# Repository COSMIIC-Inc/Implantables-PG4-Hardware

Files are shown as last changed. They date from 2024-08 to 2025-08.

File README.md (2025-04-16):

# Implantables-PG4-Hardware Read Me

## Contents
This repository is home to the 3D CAD and PCB design files of the PG4 - Pulse Generator Module in the COSMIIC System.
Further documentation is available at **[docs.cosmiic.org/Implantables/PG4-Module](https://docs.cosmiic.org/Implantables/PG4-Module)**

## Licensing
Hardware-related files are licensed to open source users by COSMIIC under the CERN Open Hardware License - Permissive - v2 (CERN-OHL-P-2.0). Refer to the **[license text](https://ohwr.org/cern_ohl_p_v2.txt)** (also embedded in the repository as **LICENSE.txt**) and **[user guide](https://ohwr.org/project/cernohl/-/wikis/uploads/8a6b5d01f71c207c49493e4d114d61e6/cern_ohl_p_v2_howto.pdf)** to understand your permissions.

Hardware-related files includes, but is not limited to...

- Mechanical Design
    - 3D CAD Files (parts and assemblies, multiple file types)
    - Mechanical Drawings (parts and assemblies, mulitple file types)
- PCB Design
    - Fabrication (Gerber and Drill files)
    - Assembly (Pick and Place, BOM)
    - Archive (Schematics, multiple file types)

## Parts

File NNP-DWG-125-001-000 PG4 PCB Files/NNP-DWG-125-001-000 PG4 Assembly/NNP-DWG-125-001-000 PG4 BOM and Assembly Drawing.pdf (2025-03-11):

D | D

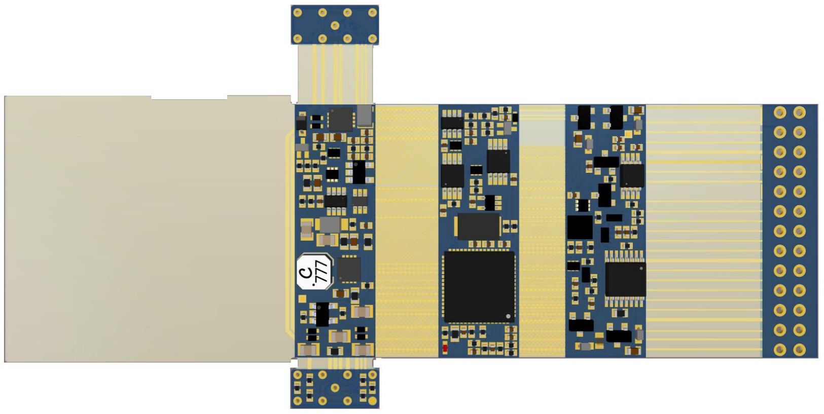
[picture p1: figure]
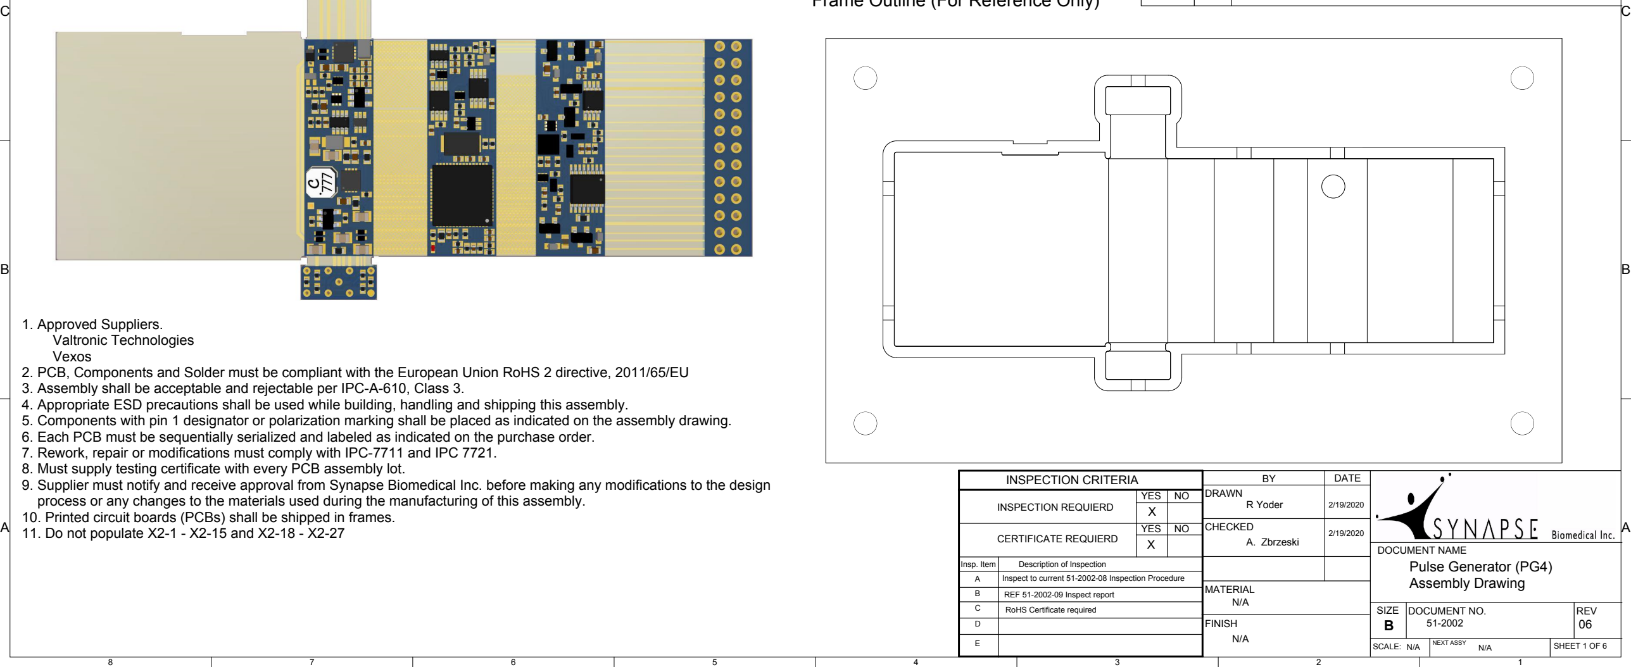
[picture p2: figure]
1. Approved Suppliers. Valtronic Technologies Vexos; CHECKED A. Zbrzeski; DRAWN R Yoder; Pulse Generator (PG4) Assembly Drawing; DOCUMENT NAME; DOCUMENT NO.; REV; NEXT ASSY; SCALE:; SIZE; FINISH; MATERIAL; DATE; SHEET 1 OF 6; RoHS Certificate required; Insp. Item; Description of Inspection; CERTIFICATE REQUIERD; YES; INSPECTION REQUIERD; INSPECTION CRITERIA; REF 51-2002-09 Inspect report

2. PCB, Components and Solder must be compliant with the European Union RoHS 2 directive, 2011/65/EU
3. Assembly shall be acceptable and rejectable per IPC-A-610, Class 3.
4. Appropriate ESD precautions shall be used while building, handling and shipping this assembly.
5. Components with pin 1 designator or polarization marking shall be placed as indicated on the assembly drawing.
6. Each PCB must be sequentially serialized and labeled as indicated on the purchase order.
7. Rework, repair or modifications must comply with IPC-7711 and IPC 7721.
8. Must supply testing certificate with every PCB assembly lot.
9. Supplier must notify and receive approval from Synapse Biomedical Inc. before making any modifications to the design
process or any changes to the materials used during the manufacturing of this assembly.
10. Printed circuit boards (PCBs) shall be shipped in frames.
11. Do not populate X2-1 - X2-15 and X2-18 - X2-27 | 2/19/2020
ECN | REV | DESCRIPTION

DCN-105
01 | Initial Engineering Release, Never Built
| 02 | Updated manufacture notes.Never released
| 03
- Updated BOM (refer to Page 1 of the Schematic for changes)
- Added component placement.
- Added Frame and PCB outline drawing.
- Added instructions for serial number sticker.

DCN-108

DCN-109 04
- Update BOM (Revision 5 of 52-2002)
- Added Quantity (Qty) column to BOM
- Corrected Note 8 Manufacture note defining test certificate

## Top Side View (For Reference Only)

- Updated notes
- Added text to Page 1 indicating that the drawings were top side view and for reference only.
- Changed text in the Material, Finish, Scale and Next Assy blocks to N/A
- Added Pin 1 designators to the components on the component placement drawing (Page 5)
- Changed component U24 from a SC70-3 package to a
SOT23-3 package to match footprint on the PCB
- Inspection Criteria box added to drawing.
- Requirements added to the Inspection Criteria Box.

DCN-119 05

## Frame Outline (For Reference Only)

A | Inspect to current 51-2002-08 Inspection Procedure

06

- Changed C33 from a 330pF to 330nF (0.33uF)
- Item 15 on BOM (02-19-2020)

D | D
C | C
B | B
A | A
DRAWN R Yoder | 2/19/2020
CHECKED A. Zbrzeski | 2/19/2020

Pulse Generator (PG4)

DOCUMENT NAME

BY | DATE

Item

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
Designator
Ref.

Ref.

Ref.

C1, C6
C2, C14, C15, C30, C38,
C40, C41, C42
C3, C5, C29
C4
C7, C8, C9, C10, C13, C18, C20, C22, C23, C24, C25,
C26, C28, C32, C34, C43,
C44, C45, C47
C11
C12, C17, C46, C48, C49
C16
C19, C21
C27
C31
C33
D1, D2, D3, D4, D5, D6, D7 D8

D9, D10, D11, D12
L1
L2
L3
LED1

Q1, Q2

Q3, Q4, Q5, Q6, Q7

R1, R2, R4, R5, R7, R8, R10, R11, R13

SBI
51-2002-01_03

52-2002_05

51-2002-07_01

56-0036
53-0037

53-0038
53-0039
53-0040

53-0041-1
53-0042
53-0043
53-0044
53-0041-2
53-0041-3
53-0047
54-0075
54-0076

54-0077
53-0032
53-0033
53-0034
53-0035

54-0050

54-0051

53-0048

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
Description
51-2002-01_03 Pulse Generator (PG4) Schematic Drawing
52-2002_05, NNP Pulse Generator PCB, Unpopulated
51-2002-07_01 Pulse Generator (PG4) Pick and Place File
0.1uF, 100V, X7R, 0805, 10%, RoHS 1uF, 50V, X5R, 10%, 0603, RoHS

47uF, 10V, X5R, 20%, 0805, RoHS 10uF, 6.3V, X5R, 0603_20%, RoHS 0.1uF, 16V, X7R, 0402, RoHS

68pF, 50V, C0G, 0402, 5%, RoHS 4.7uF, 6.3V, X5R, 20%, 0402, RoHS 0.001uF, 50V, X7R, 20%, 0402, RoHS 8pF, 50V, C0G, 0402, 10%, RoHS 1000pF, 50V, C0G, 5%, 0402, RoHS 10pF, 50V, C0G, 5%, 0402, RoHS 0.33uF, 50V, X7R, 10%, 0805, RoHS Schotty Diode, 30V, 100mA, RoHS Schottky Diode, 100V, 150mA, SOD323, RoHS
Zener Diode, 4.7V, 150 mW, 0603, RoHS 100uH, 270mA, 20%, RoHS
470uH, 35mA, 10%, RoHS
33uH, 120mA, 10%, RoHS
LED, Red, 0402, 20mA ,2V, 140mcd, RoHS
PNP, -50V, -100mA, SOT523, 150MHz, RoHS
N-Channel MOSFET, 50V, 300mA, SOT23, RoHS
0.0 ohm, 1/16W, 0402, RoHS

Manufacturer

N/A

N/A

Murata Electronics North America Murata Electronics North America

Murata Electronics North America Murata Electronics North America AVX Corporation

Murata Electronics North America Murata Electronics North America Murata Electronics North America Murata Electronics North America Murata Electronics North America Murata Electronics North America Murata Electronics North America Panasonic Electronic Components STMicroelectronics

Comchip Technology
TDK Corporation
Taiyo Yuden
TDK Corporation
Lumex Opto/Components Inc.

Panasonic Electronic Components

Diodes Incorporated

Vishay Dale

Manufacturer Part Number

N/A

N/A

GCM21BR72A104KA37K
GRT188R61H105KE13D

GRM21BR61A476ME15L
GRM188R60J106ME47J
04023C104KAT2A

GRM1555C1H680JA01D
GRM155R60J475ME47D
GJM1555C1H1R0BB01D
GRM1555C1H8R0DA01D
GRM1555C1H102JA01D
GRM1555C1H100JA01D
GRM219R71H334KA88D
DB2731600L
BAT46JFILM

CZRU52C4V7
VLCF5020T-101MR27
CB2518T471K
NLCV25T-330K-PF
SML-LX0402SIC-TR

DSA9001S0L

DMN5L06K-7

CRCW04020000Z0ED

Suggested Supplier

Innovative Circuits

N/A

Digi-Key
Digi-Key

Digi-Key
Digi-Key
Digi-Key

Digi-Key
Digi-Key
Digi-Key
Digi-Key
Digi-Key
Digi-Key
Digi-Key
Digi-Key
Digi-Key

Digi-Key
Digi-Key
Digi-Key
Digi-Key
Digi-Key

Digi-Key

Digi-Key

Digi-Key

Supplier Part Number

N/A

N/A

490-8051-6-ND
490-12330-6-ND

490-9961-6-ND
490-6405-6-ND
478-7868-6-ND

490-5876-6-ND
490-5915-6-ND
490-6073-6-ND
490-5867-6-ND
490-3244-6-ND
490-5921-6-ND
490-3327-6-ND
DB2731600LDKR-ND
497-6653-6-ND

641-1028-6-ND
445-3203-6-ND
587-2194-6-ND
445-1759-6-ND
67-1878-6-ND

DSA9001S0LDKR-ND

DMN5L06KDIDKR-ND

541-0.0JDKR-ND

D | D
C | C
B | B
A | A
BY | DATE
DRAWN R Yoder | 2/19/2020
CHECKED A. Zbrzeski | 2/19/2020

DOCUMENT NAME
Pulse Generator (PG4)

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
R15, R16, R34, R47, R48,
R60
R17, R22, R23, R24, R27,
R30, R46
R18

R19, R25, R26, R28
R20, R21

R29
R31, R38, R40, R41, R42,
R57, R58, R59, R61, R62,
R63, R64, R65, R66
R32, R35, R36, R39, R43

R37, R52

R44

R45, R56

R49
R51
R53
R54
R67
RV1
U1
U2, U3

U4

U5

53-0049-1
53-0050

53-0049-2

53-0049-3

53-0049-4
53-0049-5

53-0051
53-0049-7

53-0049-8

53-0049-9

53-0049-10

53-0049-11

53-0049-12
53-0049-13
53-0049-14
53-0049-15
53-0049-16
53-0066
54-0052
54-0053

54-0054

54-0055

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
0.1 ohm, 1%, 1/16W, 0402, RoHS 0.0 ohm, 1/10W, 0603, RoHS

49.9k ohm, 1%, 1/16W, 0402, RoHS

470k ohm, 1% , 1/16W, smd, 0402, RoHS
1.0k ohm, 1%, 1/16W, smd, 0402, RoHS 5.1K ohm, 1%, 1/16W, smd, 0402, RoHS
84.5k ohm, 1%, 1/10W, 0402, RoHS 100k ohm, 1%, 1/16W, smd, 0402, RoHS

10.0k ohm, 1%, 1/16W, smd, 0402, RoHS
15.0k ohm, 1%, 1/16W, smd, 0402, RoHS
1.6K ohm, 1%, 1/16W, smd, 0402, RoHS
150k ohm, 1%, 1/16W, smd, 0402, RoHS
10 ohm, 1%, 1/16W, 0402, RoHS 20k ohm, 1%, 1/16W, 0402, RoHS 953k ohm, 1%, 1/16W, 0402, RoHS 36k ohm , 1%, 1/16W, 0402, RoHS 56 ohm, 0.1%, 1/16W, 0402, RoHS MOV, 12V, 0603, RoHS
Current Monitor, 2.5V-20V, 1%, RoHS Step Down DC-DC, 4.5V-45V, 50mA, RoHS
Comparator, 2.7-5.5V, 40nS, SOT23-8, RoHS
XOR, 1.65-5.5V, uPAK6, RoHS

Vishay Dale
Vishay Dale

Vishay Dale

Vishay Dale

Vishay Dale
Vishay Dale

Vishay Dale
Vishay Dale

Vishay Dale

Vishay Dale

Vishay Dale

Vishay Dale

Vishay Dale
Vishay Dale
Vishay Dale
Vishay Dale
Vishay Dale
BOURNS
Diodes Incorporated
Linear Technology

Maxim Integrated

Fairchild Semiconductor

RCWE0402R100FNEA
CRCW06030000Z0EA

CRCW040249K9FKED

CRCW0402470KFKED

CRCW04021K00FKED
CRCW04025K10FKED

CRCW040284K5FKED
CRCW0402100KFKED

CRCW040210K0FKED

CRCW040215K0FKED

CRCW04021K60FKED

CRCW0402150KFKED

CRCW040210R0FKED
CRCW040220K0FKED
CRCW0402953RFKED
CRCW040236K0FKED
CRCW040256R0FKED
CG0603MLC-12E
ZXCT1010E5TA
LTC3642EDD-3.3#PBF

MAX9142EKA+T

NC7SZ86L6X

Digi-Key
Digi-Key

Digi-Key

Digi-Key

Digi-Key
Digi-Key

Digi-Key
Digi-Key

Digi-Key

Digi-Key

Digi-Key

Digi-Key

Digi-Key
Digi-Key
Digi-Key
Digi-Key
Digi-Key
Digi-Key
Digi-Key
Digi-Key

Digi-Key

Digi-Key

541-2711-6-ND
541-0.0GDKR-ND

541-49.9KLDKR-ND

541-470KLDKR-ND

541-1.00KLDKR-ND
541-5.10KLDKR-ND

541-84.5KLDKR-ND
541-100KLDKR-ND

541-10.0KLDKR-ND

541-15.0KLDKR-ND

541-1.60KLDKR-ND

541-150KLDKR-ND

541-10.0LDKR-ND
541-20.0KLDKR-ND
541-953LDKR-ND
541-36.0KLDKR-ND
541-56.0LDKR-ND
CG0603MLC-12EDKR-ND
ZXCT1010DKR-ND
LTC3642EDD-3.3#PBF-ND

MAX9142EKA+TDKR-ND

NC7SZ86L6XDKR-ND

D | D
C | C
B | B
A | A
DRAWN R Yoder | 2/19/2020
CHECKED A. Zbrzeski | 2/19/2020

Pulse Generator (PG4)

DOCUMENT NAME

BY | DATE

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
U20, U21

U22
U23
U24
Y1

54-0056
54-0057
54-0058
54-0059

54-0060
54-0061

54-0062

54-0074

54-0063

54-0064

54-0065
54-0066
54-0067

54-0068

54-0069

54-0070
54-0071
54-0072
54-0073

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
Digital Isolator, 3-5.5V, uSOP8, RoHS Silicon delay, 3-3.6V, uSOP8, RoHS FLIPFLOP, 1.65-5.5V, uPAk6, RoHS Low Droupout negative regulator, -5V, -200mA, RoHS
Voltage detector Reset, SC70-5, RoHS uC, 2.7-5.5V, 8bit, QFN64, RoHS

Temperature Sensor,12bit I2C, SOT563, RoHS
Tri-axis accelerometer, I2C, LGA10, RoHS
BOOST, 2.3-10V, TSOT23-8, RoHS

DAC 2V5 internal reference, RoHS

2-Input NOR, 1.65-5.5V, uPak6, RoHS MOSFET 2N, 60V, 0.305A, RoHS 2-Input Positive OR, 1.65-5.5V, uBGA8, RoHS
Analog Switch, 10ohm, QUAD SPST, TSSOP16, RoHS
Dual 2-Input NOR, 1.65-5.5V, uBGA8, RoHS
UHS Buffer Tri-State, uPAK6, RoHS DAC 10bit, uSOP8, RoHS
REF 1.25V, 3.9uA, SOT23-3, RoHS Crystal 8MHz SMT, RoHS

NVE Corp/Isolation Products Maxim Integrated
Fairchild Semiconductor
Linear Technology

Texas Instruments
Atmel

Texas Instruments

Kionix

Linear Technology

Linear Technology

Fairchild Semiconductor
Vishay Siliconix
Texas Instruments

Maxim Integrated

Texas Instruments

Fairchild Semiconductor
Maxim Integrated
Texas Instruments
NDK

IL712-1E
DS1100LU-500+
NC7SZ175L6X
LT1964IS5-BYP#TRMPBF

TPS3805H33DCKR
AT90CAN128-16MU

TMP112AIDRLT

KXTE9-2050

LT3464ETS8#TRMPBF

LTC2630CSC6-LM12#TRMPBF

NC7SZ02L6X
SI1026X-T1-GE3
SN74LVC2G32YZPR

MAX313LCUE+

SN74LVC2G02YZPR

NC7SZ126L6X
MAX5355CUA+
REF3312AIDBZR
NX5032GA-8.000M-STD-CSU-1

Digi-Key
Digi-Key
Digi-Key
Digi-Key

Digi-Key
Digi-Key

Digi-Key

Mouser

Digi-Key

Digi-Key

Digi-Key
Digi-Key
Digi-Key

Digi-Key

Digi-Key

Digi-Key
Digi-Key
Digi-Key
Digi-Key

390-1105-5-ND
DS1100LU-500+-ND
NC7SZ175L6XFSDKR-ND
LT1964IS5-
BYP#TRMPBFCT-ND
296-13407-6-ND
AT90CAN128-16MURDKR-ND
296-24621-6-ND

912-KXTE9-2050

LT3464ETS8#TRMPBFDKR-ND
LTC2630CSC6-
LM12#TRMPBFDKR-ND
NC7SZ02L6XDKR-ND
SI1026X-T1-GE3CT-ND
296-15350-1-ND

MAX313LCUE+-ND

296-18799-6-ND

NC7SZ126L6XFSDKR-ND
MAX5355CUA+-ND
296-41484-6-ND
644-1132-6-ND

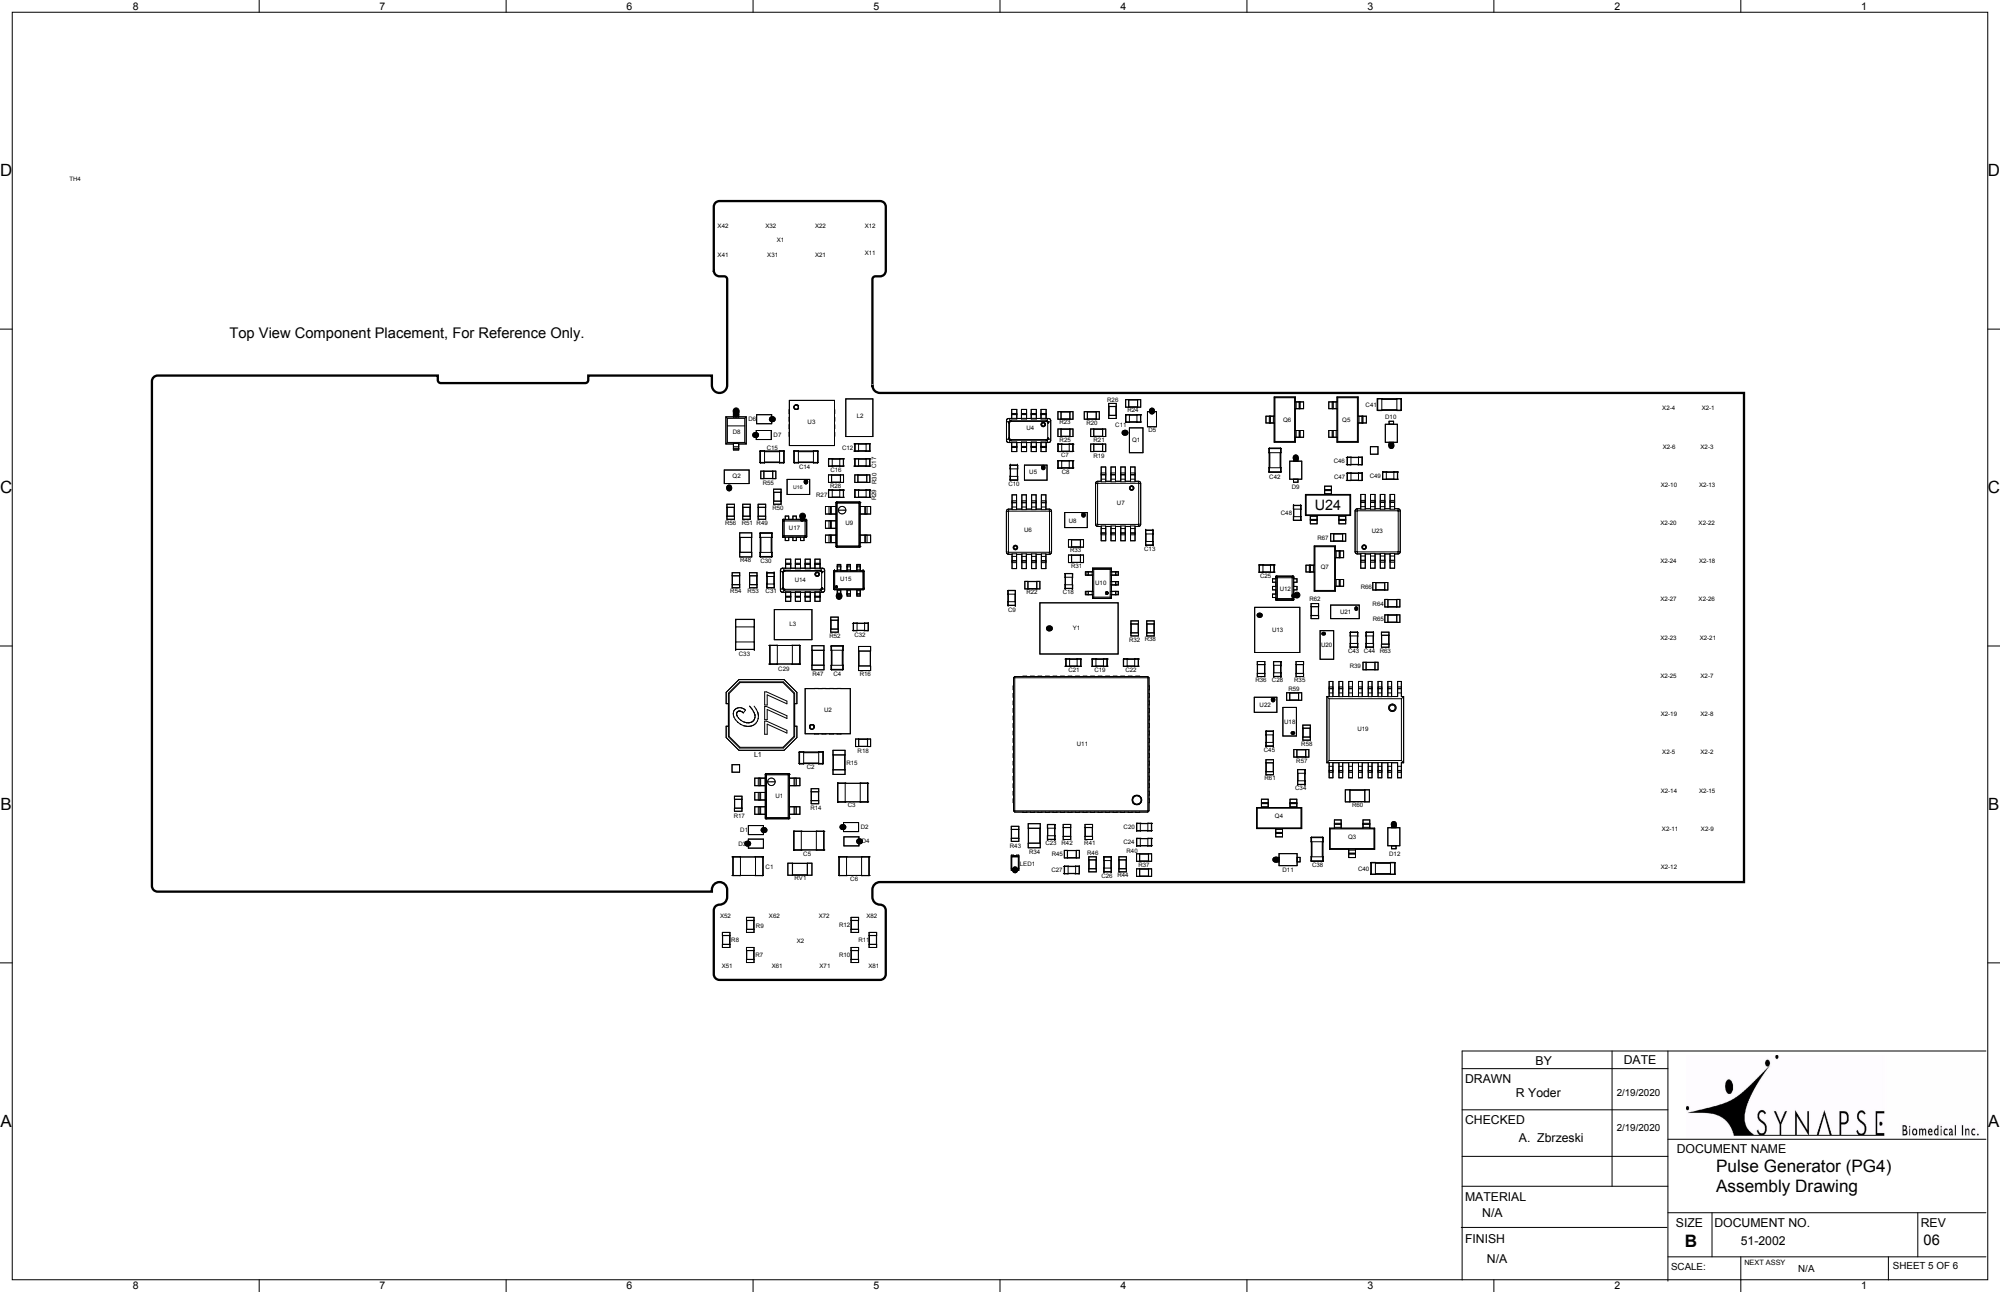
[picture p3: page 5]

Top View Component Placement, For Reference Only.

DRAWN R Yoder | 2/19/2020

CHECKED A. Zbrzeski | 2/19/2020

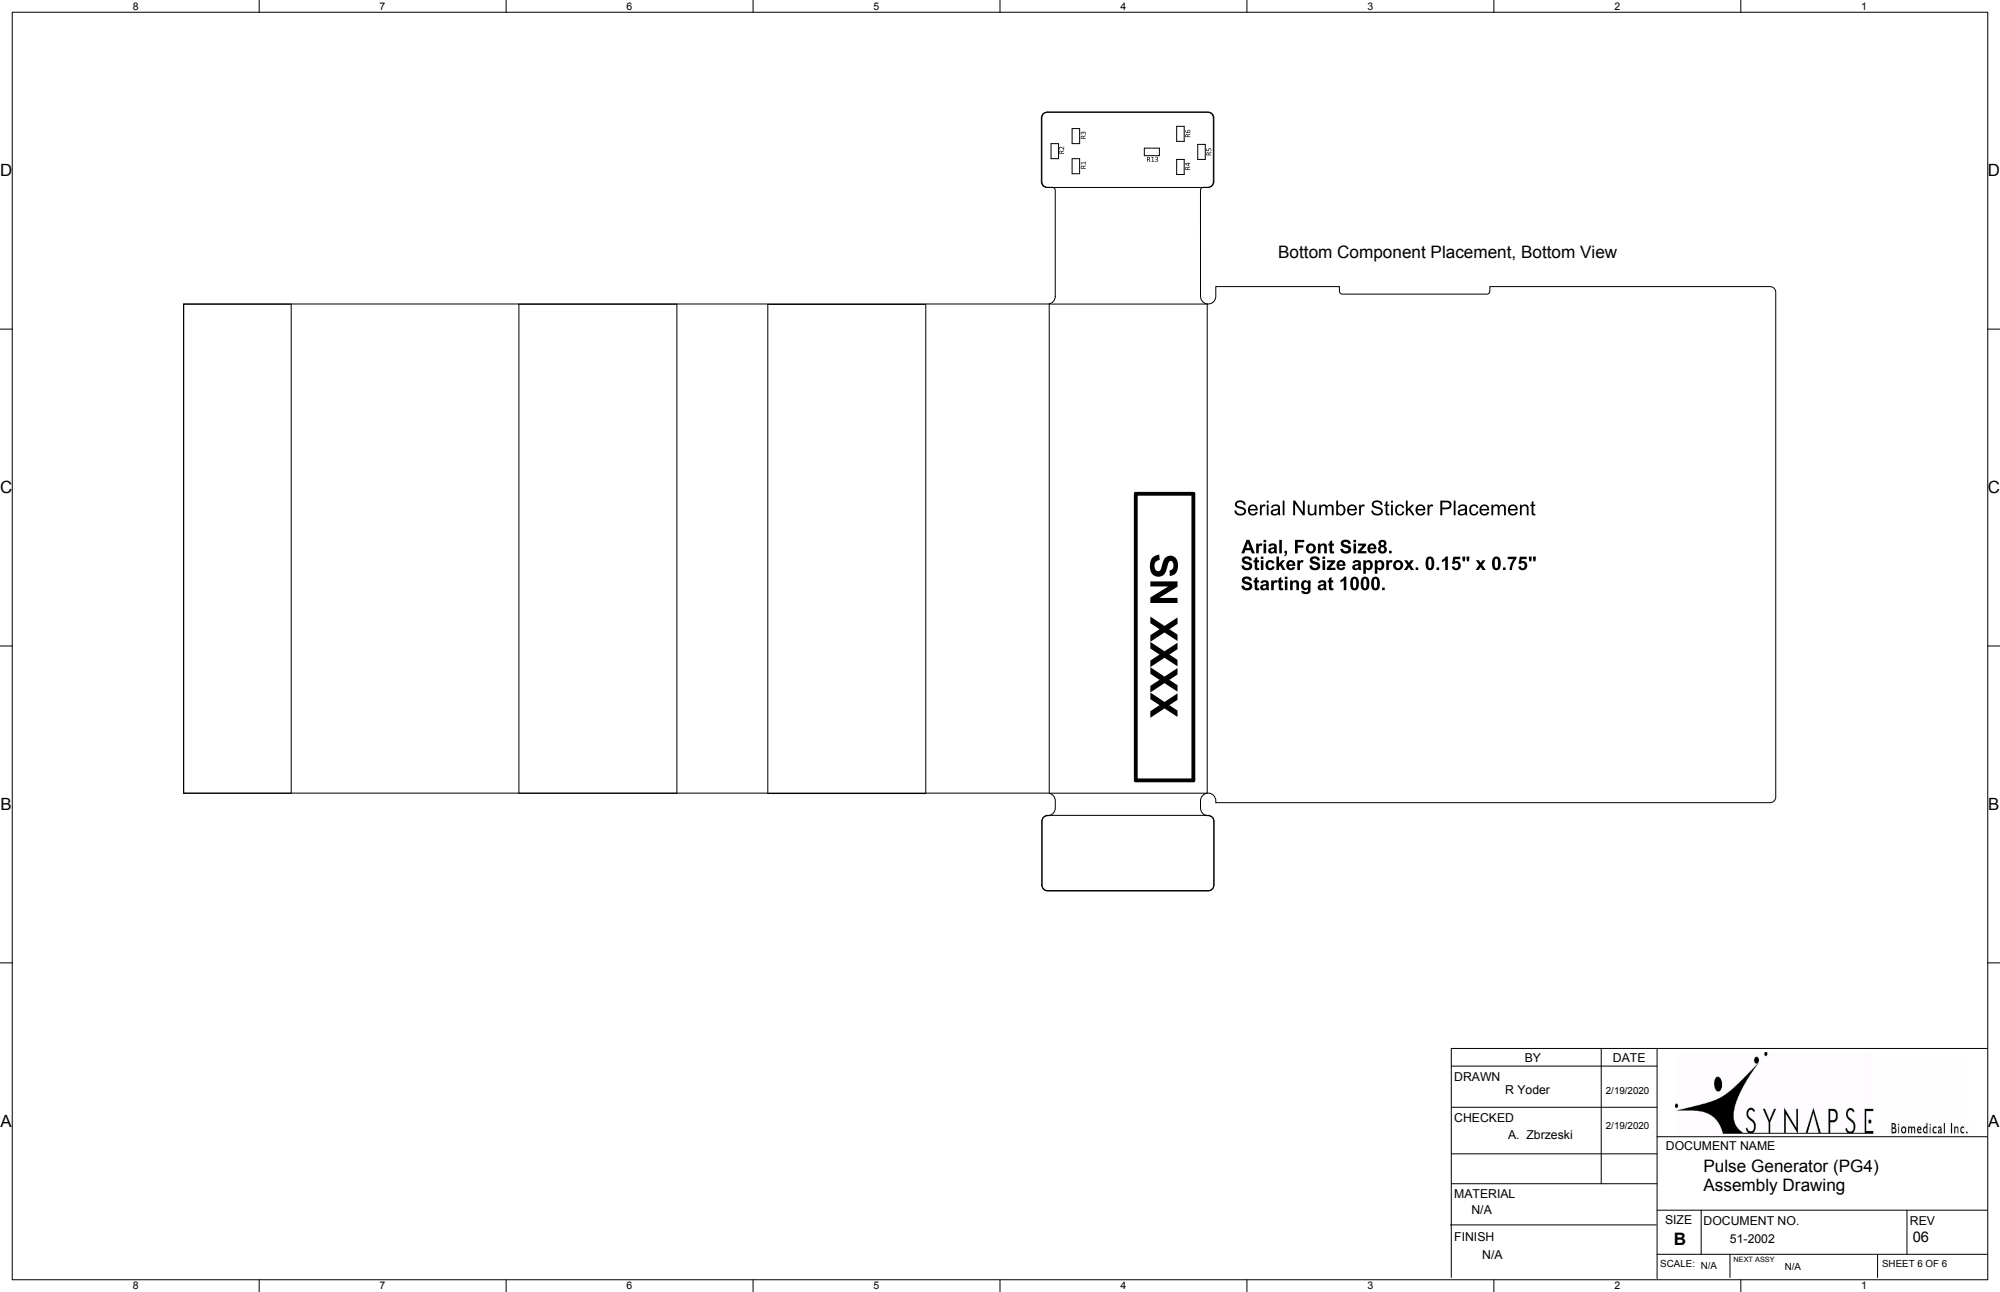
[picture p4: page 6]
DATE; DOCUMENT NAME Pulse Generator (PG4)

Bottom Component Placement, Bottom View

DRAWN R Yoder | 2/19/2020

CHECKED A. Zbrzeski | 2/19/2020

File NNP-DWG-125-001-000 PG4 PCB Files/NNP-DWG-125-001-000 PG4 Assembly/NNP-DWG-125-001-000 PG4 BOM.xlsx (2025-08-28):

Designator | Description | Quantity | MFR | MPN | Supplier 1 | Supplier Part Number 1 | Footprint
C1, C6 | 0.1uF, 100V, X7R, 0805, 10%, RoHS | 2 | AVX | 08051C104KAZ2A | Digi-Key | 478-3562-1-ND (https://octopart-clicks.com/click/altium?manufacturer=AVX%20Corporation&mpn=08051C104KAZ2A&seller=Digi-Key&sku=478-3562-1-ND&country=US&channel=BOM%20Report) | CAP_0805
C12, C19, C48, C50, C51 | 4.7uF, 6.3V, X5R, 20%, 0402, RoHS | 5 | Panasonic | ECJ-0EB0J475M | Digi-Key | PCC2475CT-ND (https://octopart-clicks.com/click/altium?manufacturer=Panasonic%20Electronic%20Components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) | CAP_0402
C13 | 68pF, 50V, C0G, 0402, 5%, RoHS | 1 | Murata | GRM1555C1H680JZ01D | Digi-Key | 490-1289-1-ND (https://octopart-clicks.com/click/altium?mpn=GRM1555C1H680JZ01D&seller=Digi-Key&sku=490-1289-1-ND&country=US&channel=BOM%20Report) | CAP_0402
C17 | 0.001uF, 50V, X7R, 20%, 0402, RoHS | 1 | Kemet | C0402C103M5RACTU | Digi-Key | 399-7760-2-ND (https://octopart-clicks.com/click/altium?manufacturer=Kemet&mpn=C0402C103M5RACTU&seller=Digi-Key&sku=399-7760-2-ND&country=US&channel=BOM%20Report) | CAP_0402
C2, C14, C15, C33, C37, C38, C39, C40, C41, C42, C43, C44 | 1uF, 50V, X5R, 10%, 0603, RoHS | 12 | Taiyo Yuden | UMK107BJ105KA-T | Digi-Key | 587-2400-1-ND (https://octopart-clicks.com/click/altium?manufacturer=Taiyo%20Yuden&mpn=UMK107BJ105KA-T&seller=Digi-Key&sku=587-2400-1-ND&country=US&channel=BOM%20Report) | CAP_0603
C21, C23 | 8pF, 50V, C0G, 0402, 10%, RoHS | 2 | Panasonic | ECJ-0EC1H080D | Digi-Key | PCC080CQCT-ND (https://octopart-clicks.com/click/altium?manufacturer=Panasonic%20Electronic%20Components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) | CAP_0402
C29 | 1000pF, 50V, C0G, 5%, 0402, RoHS | 1 | Murata | GRM1555C1H102JA01D | Digi-Key | 490-3244-1-ND (https://octopart-clicks.com/click/altium?mpn=GRM1555C1H102JA01D&seller=Digi-Key&sku=490-3244-1-ND&country=US&channel=BOM%20Report) | CAP_0402
C32 | 10pF, 50V, C0G, 5%, 0402, RoHS | 1 | Murata | GRM1555C1H100JZ01 | Digi-Key | 490-1278-1-ND (https://octopart-clicks.com/click/altium?mpn=GRM1555C1H100JZ01D&seller=Digi-Key&sku=490-1278-1-ND&country=US&channel=BOM%20Report) | CAP_0402
C35 | 0.33uF, 50V, X7R, 10%, 0805, RoHS | 1 | Murata | GRM219R71H334KA88D | Digi-Key | 490-3327-1-ND (https://octopart-clicks.com/click/altium?mpn=GRM219R71H334KA88D&seller=Digi-Key&sku=490-3327-1-ND&country=US&channel=BOM%20Report) | CAP_0805
C4 | 10uF, 6.3V, X5R, 0603_20%, RoHS | 1 | Panasonic | ECJ-1VB0J106M | Digi-Key | PCC2395CT-ND (https://octopart-clicks.com/click/altium?manufacturer=Panasonic%20Electronic%20Components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) | CAP_0603
C3, C5, C31 | 47uF 10V, X5R, 20%, 0805, RoHS | 3 | TDK | C2012X5R1A476M125AC | Digi-Key | 445-8239-6-ND (https://octopart-clicks.com/click/altium?manufacturer=TDK%20Corporation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) | CAP_0805
C7, C8, C9, C10, C11, C20, C22, C24, C25, C26, C27, C28, C30, C34, C36, C45, C46, C47, C49 | 0.1uF, 16V, X7R, 0402, RoHS | 19 | Murata | GRM155R71C104KA88D | Digi-Key | 490-3261-2-ND (https://octopart-clicks.com/click/altium?mpn=GRM155R71C104KA88D&seller=Digi-Key&sku=490-3261-2-ND&country=US&channel=BOM%20Report) | CAP_0402
D1, D2, D3, D4, D5, D6, D7 | Schotty Diode, 30V, 100mA, RoHS | 7 | Panasonic | DB27316 | Digi-Key | DB2731600LCT-ND (https://octopart-clicks.com/click/altium?manufacturer=Panasonic%20Electronic%20Components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) | SSSMini2-F4-B
D8 | Schottky Diode, 100V, 150mA, SOD323, RoHS | 1 | STMicroelectronics | BAT46JFILM | Digi-Key | 497-6653-1-ND (https://octopart-clicks.com/click/altium?manufacturer=STMicroelectronics&mpn=BAT46JFILM&seller=Digi-Key&sku=497-6653-1-ND&country=US&channel=BOM%20Report) | SOD323
L1 | 100uH, 270mA, 20%, RoHS | 1 | TDK | LPS4414-104MLC | Digi-Key | 445-3203-1-ND (https://octopart-clicks.com/click/altium?manufacturer=TDK%20Corporation&mpn=VLCF5020T-101MR27&seller=Digi-Key&sku=445-3203-1-ND&country=US&channel=BOM%20Report) | IND-LPS4414
L2 | 470uH, 35mA, 10%, RoHS | 1 | Taiyo Yuden | CB2518T471K | Digi-Key | 587-2194-6-ND (https://octopart-clicks.com/click/altium?manufacturer=Taiyo%20Yuden&mpn=CB2518T471K&seller=Digi-Key&sku=587-2194-6-ND&country=US&channel=BOM%20Report) | IND_1007
L3 | 33uH, 120mA, 10%, RoHS | 1 | Panasonic | ELJ-PC330KF | Digi-Key | PCD1096CT-ND (https://octopart-clicks.com/click/altium?manufacturer=Panasonic%20Electronic%20Components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) | IND_1008
LED1 | LED, Red, 0402, 20mA ,2V, 140mcd, RoHS | 1 | Lumex | SML-LX0402SIC-TR | Digi-Key | 67-1878-1-ND (https://octopart-clicks.com/click/altium?manufacturer=Lumex%20Opto%2FComponents%20Inc.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) | LED_0402_RED
Q1, Q2 | PNP, -50V, -100mA, SOT523, 150MHz, RoHS | 2 | Panasonic | DSA9001S0L | Digi-Key | DSA9001S0LDKR-ND (https://octopart-clicks.com/click/altium?manufacturer=Panasonic%20Electronic%20Components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) | SOT523
Q3, Q4, Q5, Q6, Q7 | N-Channel MOSFET, 50V, 300mA, SOT23, RoHS | 5 | Diodes Inc. | DMN5L06K-7 | Digi-Key | DMN5L06KDICT-ND (https://octopart-clicks.com/click/altium?manufacturer=Diodes%20Incorporated&mpn=DMN5L06K-7&seller=Digi-Key&sku=DMN5L06KDICT-ND&country=US&channel=BOM%20Report) | SOT23-3
R? | 84.5k ohm, 1%, 1/10W, 0402, RoHS | 1 | Panasonic | ERJ-2RKF8452X | Digi-Key | P84.5KLTR-ND (https://octopart-clicks.com/click/altium?manufacturer=Panasonic%20Electronic%20Components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) | CAP_0402
R1, R2, R4, R5, R7, R8, R10, R11, R13 | 0.0 ohm, 1/16W, 0402, RoHS | 9 | Rohm | MCR01MZPJ000 | Digi-Key | RHM0.0JCT-ND (https://octopart-clicks.com/click/altium?manufacturer=Rohm%20Semiconductor&mpn=MCR01MZPJ000&seller=Digi-Key&sku=RHM0.0JCT-ND&country=US&channel=BOM%20Report) | RES_0402
R14 | 0.1 ohm, 1%, 1/16W, 0402, RoHS | 1 | Susumu | RP1005S-R10-F | Digi-Key | RP10S.10FCT-ND (https://octopart-clicks.com/click/altium?manufacturer=Susumu&mpn=RP1005S-R10-F&seller=Digi-Key&sku=RP10S.10FCT-ND&country=US&channel=BOM%20Report) | RES_0402
R15, R16, R31, R45, R46, R58 | 0.0 ohm, 1/10W, 0603, RoHS | 6 | Rohm | MCR03ERTJ000 | Digi-Key | RHM0.0CGCT-ND (https://octopart-clicks.com/click/altium?manufacturer=Rohm%20Semiconductor&mpn=MCR03ERTJ000&seller=Digi-Key&sku=RHM0.0CGCT-ND&country=US&channel=BOM%20Report) | RES_0603
R17, R22, R23, R24, R28, R44, R66 | 49.9k ohm, 1%, 1/16W, 0402, RoHS | 7 | Rohm | MCR01MZPF4992 | Digi-Key | RHM49.9KLCT-ND (https://octopart-clicks.com/click/altium?manufacturer=Rohm%20Semiconductor&mpn=MCR01MZPF4992&seller=Digi-Key&sku=RHM49.9KLCT-ND&country=US&channel=BOM%20Report) | RES_0402
R18 | 470k ohm, 1/16W, smd, 0402, RoHS | 1 | Panasonic | ERJ-2RKF4703X | Digi-Key | P470KLTR-ND (https://octopart-clicks.com/click/altium?manufacturer=Panasonic%20Electronic%20Components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) | RES_0402
R19, R25, R26, R27 | 1.0k ohm, 1%, 1/16W, smd, 0402, RoHS | 4 | Rohm | MCR01MZPF1001 | Digi-Key | RHM1.00KLCT-ND (https://octopart-clicks.com/click/altium?manufacturer=Rohm%20Semiconductor&mpn=MCR01MZPF1001&seller=Digi-Key&sku=RHM1.00KLCT-ND&country=US&channel=BOM%20Report) | RES_0402
R20, R21 | 5.1K ohm, 1/16W, smd, 0402, RoHS | 2 | Rohm | MCR01MZPF5101 | Digi-Key | RHM5.10KLCT-ND (https://octopart-clicks.com/click/altium?manufacturer=Rohm%20Semiconductor&mpn=MCR01MZPF5101&seller=Digi-Key&sku=RHM5.10KLCT-ND&country=US&channel=BOM%20Report) | RES_0402
R29, R36, R37, R39, R40, R55, R56, R57, R59, R60, R61, R62, R63, R64 | 100k ohm, 1/16W, smd, 0402, RoHS | 14 | Rohm | MCR01MZPF1003 | Digi-Key | RHM100KLCT-ND (https://octopart-clicks.com/click/altium?manufacturer=Rohm%20Semiconductor&mpn=MCR01MZPF1003&seller=Digi-Key&sku=RHM100KLCT-ND&country=US&channel=BOM%20Report) | RES_0402
R30, R33, R34, R38, R41 | 10.0k ohm, 1/16W, smd, 0402, RoHS | 5 | Rohm | MCR01MZPF1002 | Digi-Key | RHM10.0KLCT-ND (https://octopart-clicks.com/click/altium?manufacturer=Rohm%20Semiconductor&mpn=MCR01MZPF1002&seller=Digi-Key&sku=RHM10.0KLCT-ND&country=US&channel=BOM%20Report) | RES_0402
R35, R50 | 15.0k ohm, 1/16W, smd, 0402, RoHS | 2 | Rohm | MCR01MZPF1502 | Digi-Key | RHM15.0KLCT-ND (https://octopart-clicks.com/click/altium?manufacturer=Rohm%20Semiconductor&mpn=MCR01MZPF1502&seller=Digi-Key&sku=RHM15.0KLCT-ND&country=US&channel=BOM%20Report) | RES_0402
R42 | 1.6K ohm, 1/16W, smd, 0402, RoHS | 1 | Vishay | CRCW04021K60FKED | Digi-Key | 541-1.60KLCT-ND (https://octopart-clicks.com/click/altium?manufacturer=Vishay%20Dale&mpn=CRCW04021K60FKED&seller=Digi-Key&sku=541-1.60KLCT-ND&country=US&channel=BOM%20Report) | RES_0402
R43, R54 | 150k ohm, 1/16W, smd, 0402, RoHS | 2 | Rohm | MCR01MZPF1503 | Digi-Key | RHM150KLCT-ND (https://octopart-clicks.com/click/altium?manufacturer=Rohm%20Semiconductor&mpn=MCR01MZPF1503&seller=Digi-Key&sku=RHM150KLCT-ND&country=US&channel=BOM%20Report) | RES_0402
R47 | 10 ohm, 1%, 1/16W, 0402, RoHS | 1 | Rohm | MCR01MZPF10R0 | Digi-Key | RHM10.0LCT-ND (https://octopart-clicks.com/click/altium?manufacturer=Rohm%20Semiconductor&mpn=MCR01MZPF10R0&seller=Digi-Key&sku=RHM10.0LCT-ND&country=US&channel=BOM%20Report) | RES_0402
R49 | 20k ohm, 1%, 1/16W, 0402, RoHS | 1 | Rohm | MCR01MZPF2002 | Digi-Key | RHM20.0KLCT-ND (https://octopart-clicks.com/click/altium?manufacturer=Rohm%20Semiconductor&mpn=MCR01MZPF2002&seller=Digi-Key&sku=RHM20.0KLCT-ND&country=US&channel=BOM%20Report) | RES_0402
R51 | 953k ohm, 1%, 1/16W, 0402, RoHS | 1 | Vishay | CRCW0402953KFKED | Digi-Key | 541-953KLCT-ND (https://octopart-clicks.com/click/altium?manufacturer=Vishay%20Dale&mpn=CRCW0402953KFKED&seller=Digi-Key&sku=541-953KLCT-ND&country=US&channel=BOM%20Report) | RES_0402
R52 | 36k ohm 1/16W smd 0402 RoHS | 1 | Rohm | MCR01MZPF3602 | Digi-Key | RHM36.0KLCT-ND (https://octopart-clicks.com/click/altium?manufacturer=Rohm%20Semiconductor&mpn=MCR01MZPF3602&seller=Digi-Key&sku=RHM36.0KLCT-ND&country=US&channel=BOM%20Report) | RES_0402
R65 | 56 ohm, 0.1%, 1/16W, 0402, RoHS | 1 | Susumu | RG1005P-560-B-T5 | Digi-Key | RG10P56BCT-ND (https://octopart-clicks.com/click/altium?manufacturer=Susumu&mpn=RG1005P-560-B-T5&seller=Digi-Key&sku=RG10P56BCT-ND&country=US&channel=BOM%20Report) | RES_0402
RV1 | MOV, 12V, 0603, RoHS | 1 | Bourns | CG0603MLC-12E | Newark | 60H7368 (https://octopart-clicks.com/click/altium?manufacturer=BOURNS&mpn=CG0603MLC-12E&seller=Newark&sku=60H7368&country=US&channel=BOM%20Report) | RES_0603
U1 | CUR 2.5-20V SOT23-5 | 1 | Zetex | ZXCT1010E5TA | Digi-Key | ZXCT1010CT-ND (https://octopart-clicks.com/click/altium?manufacturer=Diodes%20Incorporated&mpn=ZXCT1010E5TA&seller=Digi-Key&sku=ZXCT1010CT-ND&country=US&channel=BOM%20Report) | SOT23-5
U10 | RESET 1.3-6.0V SC70-5 | 1 | Texas Instruments | TPS3805H33DCKR | Digi-Key | 296-13407-1-ND (https://octopart-clicks.com/click/altium?manufacturer=Texas%20Instruments&mpn=TPS3805H33DCKR&seller=Digi-Key&sku=296-13407-1-ND&country=US&channel=BOM%20Report) | SC70-5
U11 | uC 2.7-5.5V 8bit QFN64 | 1 | Atmel | AT90CAN128-16MI | Digi-Key | AT90CAN128-16MU-ND (https://octopart-clicks.com/click/altium?manufacturer=Atmel&mpn=AT90CAN128-16MU&seller=Digi-Key&sku=AT90CAN128-16MU-ND&country=US&channel=BOM%20Report) | QFN64
U12 | TEMP 1.4-3.6V 10uA 12bit I2C SOT563 | 1 | Texas Instruments | TMP112AIDRLT | Digi-Key | 296-24621-1-ND (https://octopart-clicks.com/click/altium?manufacturer=Texas%20Instruments&mpn=TMP112AIDRLT&seller=Digi-Key&sku=296-24621-1-ND&country=US&channel=BOM%20Report) | SOT-563
U13 | ACCelerometer 3V3 30uA I2C LGA10 | 1 | Kionix | KXTE9-2050 | Kionix | KXTE9-2050 (https://octopart-clicks.com/click/altium?manufacturer=Supplier%20disabled&mpn=Supplier%20disabled&seller=Kionix&sku=KXTE9-2050&country=US&channel=BOM%20Report) | LGA10
U14 | BOOST 2.3-10V TSOT23-8 | 1 | Linear Technology | LT3464ETS8 | Digi-Key | LT3464ETS8#TRMPBFCT-ND (https://octopart-clicks.com/click/altium?manufacturer=Linear%20Technology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) | SOT23-8
U15 | DAC 2V5 internal reference | 1 | Linear Technology | LTC2630CSC6-LM12#TRMPBF | Digi-Key | LTC2630CSC6-LM12#TRMPBFCT-ND (https://octopart-clicks.com/click/altium?manufacturer=Linear%20Technology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) | SC70-6
U16 | NOR 1.65-5.5V uPak6 | 1 | Fairchild | NC7SZ02L6X | Mouser | 512-NC7SZ02L6X (https://octopart-clicks.com/click/altium?manufacturer=Fairchild%20Semiconductor&mpn=NC7SZ02L6X&seller=Mouser&sku=512-NC7SZ02L6X&country=US&channel=BOM%20Report) | uPak6
U17 | M 60 500m SOT563 Dual 1R4 | 1 | Vishay | Si1026X-T1-E3 | Digi-Key | SI1026X-T1-E3CT-ND (https://octopart-clicks.com/click/altium?manufacturer=Vishay%20Siliconix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) | SOT-563
U18 | OR 1.65-5.5V uBGA8 | 1 | Texas Instruments | SN74LVC2G32YZPR | Digi-Key | 296-15350-1-ND (https://octopart-clicks.com/click/altium?manufacturer=Texas%20Instruments&mpn=SN74LVC2G32YZPR&seller=Digi-Key&sku=296-15350-1-ND&country=US&channel=BOM%20Report) | DSBGA-8-YZP
U19 | ANA SW 36V TSSOP16 | 1 | Maxim | MAX313LCUE | Digi-Key | MAX313LCUE+-ND (https://octopart-clicks.com/click/altium?manufacturer=Maxim%20Integrated&mpn=MAX313LCUE%2B&seller=Digi-Key&sku=MAX313LCUE%2B-ND&country=US&channel=BOM%20Report) | TSSOP16
U2, U3 | BUCK 4.5-45V DFN8 | 2 | Linear Technology | LTC3642EDD-3.3#PBF | Digi-Key | LTC3642EDD-3.3#PBF-ND (https://octopart-clicks.com/click/altium?manufacturer=Linear%20Technology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) | DFN8
U20, U21 | NOR 1.65-5.5V uBGA8 | 2 | Texas Instruments | SN74LVC2G02YEAR | Digi-Key | 296-13731-1-ND (https://octopart-clicks.com/click/altium?manufacturer=Texas%20Instruments&mpn=SN74LVC2G02YEAR&seller=Digi-Key&sku=296-13731-1-ND&country=US&channel=BOM%20Report) | DSBGA-8-YZP
U22 | BUF 1.65-5.5V uPak6 | 1 | Fairchild | NC7SZ126L6X | Mouser | 512-NC7SZ126L6X (https://octopart-clicks.com/click/altium?manufacturer=Fairchild%20Semiconductor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) | uPak6
U23 | DAC 10bit uSOP8 | 1 | Maxim | MAX5355CUA+ | Digi-Key | MAX5355CUA+-ND (https://octopart-clicks.com/click/altium?manufacturer=Maxim%20Integrated&mpn=MAX5355CUA%2B&seller=Digi-Key&sku=MAX5355CUA%2B-ND&country=US&channel=BOM%20Report) | uSOP-8L
U24 | REF 1.25V 3.9uA SC70-3 | 1 | Texas Instruments | REF3312AIDCKR | Digi-Key | 296-22636-1-ND (https://octopart-clicks.com/click/altium?manufacturer=Texas%20Instruments&mpn=REF3312AIDCKR&seller=Digi-Key&sku=296-22636-1-ND&country=US&channel=BOM%20Report) | SOT23-3
U4 | CMP 2.7-5.5V 40ns SOT23-8 | 1 | Maxim | MAX9142EKA+ | Digi-Key | MAX9142EKA+TCT-ND (https://octopart-clicks.com/click/altium?manufacturer=Maxim%20Integrated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) | SOT23-8
U5 | XOR 1.65-5.5V uPAK6 | 1 | Fairchild | NC7SZ86L6X | Mouser | 512-NC7SZ86L6X (https://octopart-clicks.com/click/altium?manufacturer=Fairchild%20Semiconductor&mpn=NC7SZ86L6X&seller=Mouser&sku=512-NC7SZ86L6X&country=US&channel=BOM%20Report) | uPak6
U6 | ISO DIG 3-5.5V uSOP8 | 1 | NVE | IL712-1E | Digi-Key | 390-1105-5-ND (https://octopart-clicks.com/click/altium?manufacturer=NVE%20Corp%2FIsolation%20Products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) | uSOP-8L
U7 | Silicon delay 3-3.6V uSOP8 | 1 | Maxim | DS1100LU-500 | Maxim | DS1100LU-500 (https://octopart-clicks.com/click/altium?manufacturer=Supplier%20disabled&mpn=Supplier%20disabled&seller=Maxim&sku=DS1100LU-500&country=US&channel=BOM%20Report) | uSOP-8L
U8 | FLIPFLOP 1.65-5.5V uPAk6 | 1 | Fairchild | NC7SZ175L6X | Mouser | 512-NC7SZ175L6X (https://octopart-clicks.com/click/altium?manufacturer=Fairchild%20Semiconductor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) | uPak6
U9 | LDO -1.2-20V -200mA | 1 | Linear Technology | LT1964ES5-BYP#PBF | Digi-Key | LT1964ES5-BYP#TRMPBFCT-ND (https://octopart-clicks.com/click/altium?manufacturer=Linear%20Technology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) | SOT23-5
Y1 | Crystal 8MHz SMT | 1 | NDK | NX5032GA | Digi-Key | 644-1132-1-ND (https://octopart-clicks.com/click/altium?manufacturer=NDK&mpn=NX5032GA-8.000M-STD-CSU-1&seller=Digi-Key&sku=644-1132-1-ND&country=US&channel=BOM%20Report) | NX5032GA

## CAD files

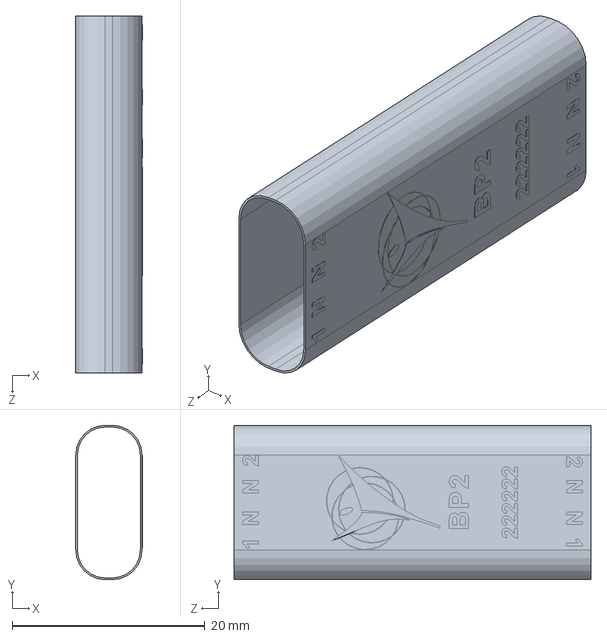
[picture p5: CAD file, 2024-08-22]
Mechanical Design CAD Files/SolidWorks Native Files/NNP-DWG-120-001-000 Remote Module, Case, PG4 Marking.SLDASM
6.91 x 16.0 x 37.1 mm

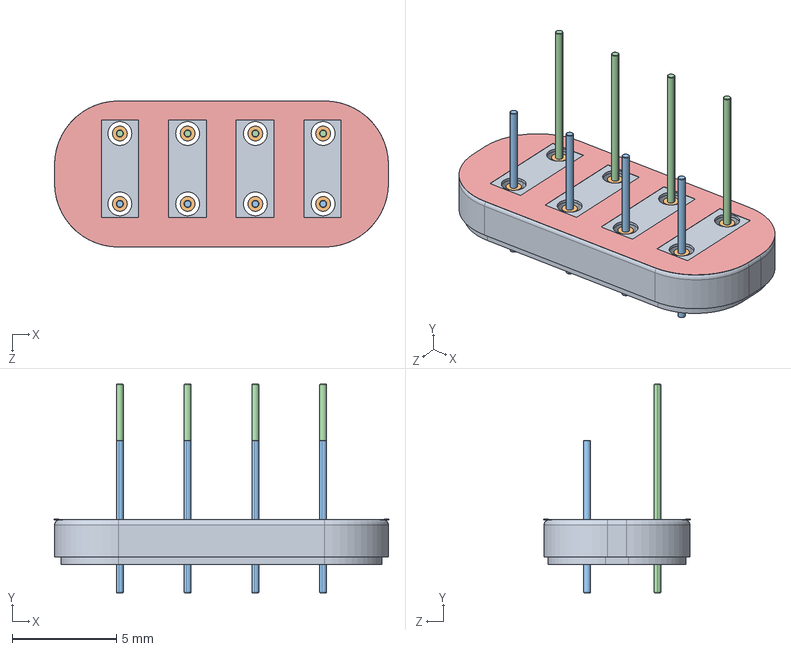
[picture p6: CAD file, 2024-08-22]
Mechanical Design CAD Files/STEP Files/NNP-DWG-135-001-001 SA, Remote Module, Capthrough Sandblasted.STEP
16.0 x 10.0 x 7.01 mm
NNP-DWG-130-010-000 Remote Module, Capthrough, Lid
NNP-DWG-130-008-000 Capthrough, Ceramic x 8
NNP-DWG-130-009-001 Capthrough, Pin, Ring x 4
NNP-DWG-130-009-002 Capthrough, Pin, Jogged_PRE-BENT x 4
NNP-MAT-150-017-000 150 Micron Aluminum Oxide

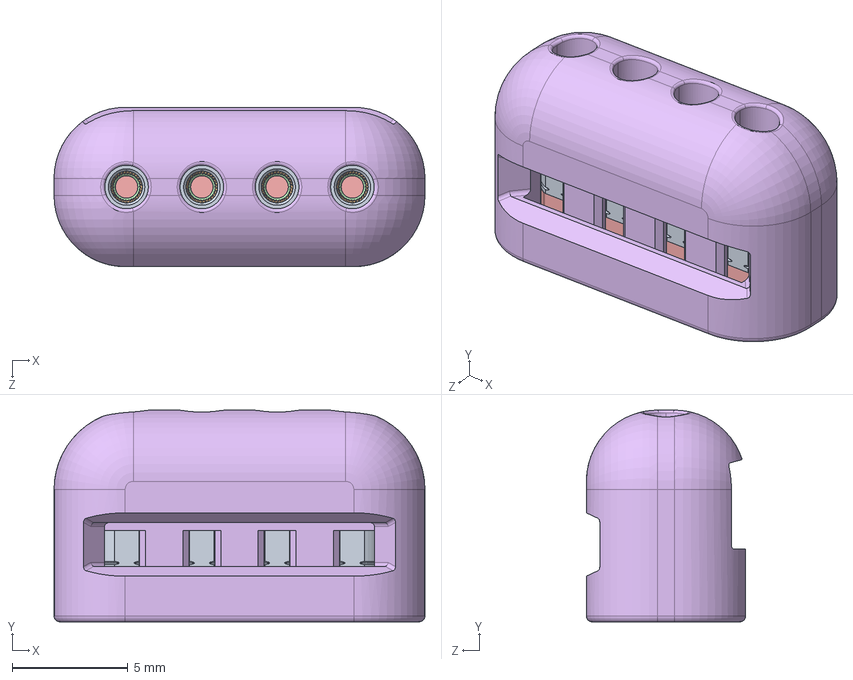
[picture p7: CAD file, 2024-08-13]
Mechanical Design CAD Files/STEP Files/NNP-DWG-135-005-000 SA, Remote Module, Header.STEP
16.0 x 9.14 x 6.88 mm
NNP-DWG-130-011-000 Balseal, Conductor x 8
NNP-DWG-130-012-001 Balseal, Spring, CW x 4
NNP-DWG-130-013-001 Balseal, Washer, CW x 4
NNP-DWG-130-013-002 Balseal, Washer, CCW x 4
NNP-DWG-130-012-002 Balseal, Spring, CCW x 4
NNP-DWG-130-005-000 BalSeal Assembly, Internal Cavity Single Seal_COMPRESSED x 4
NNP-DWG-130-004-000 Remote Module, Pre-Molded Header Cap
NNP-DWG-130-003-000 Remote Module, Pre-Molded Header Body
NNP-DWG-130-006-000 Remote Module, Header, Gasket_GASKET x 8

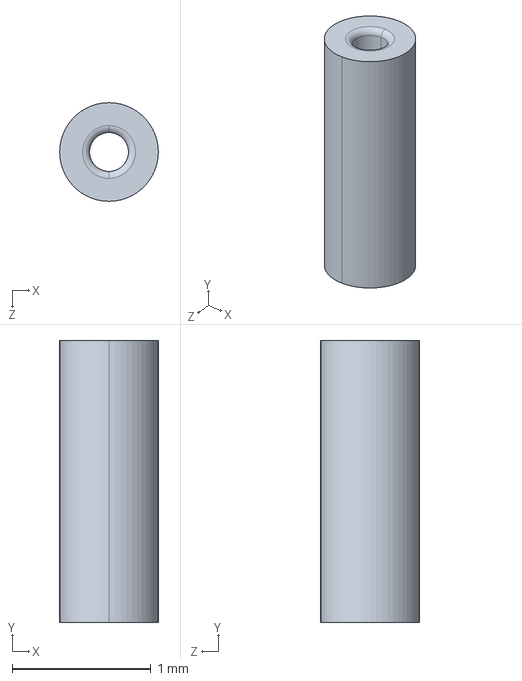
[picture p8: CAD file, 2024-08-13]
Mechanical Design CAD Files/STEP Files/NNP-DWG-130-008-000 Capthrough, Ceramic.STEP
0.711 x 2.03 x 0.711 mm

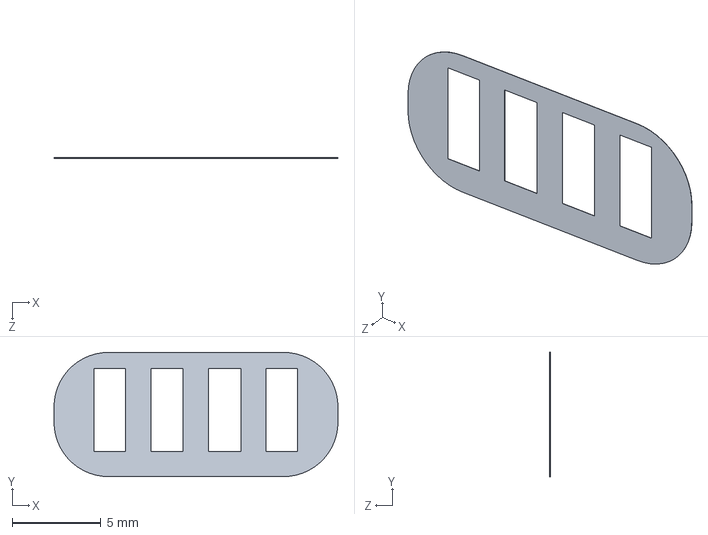
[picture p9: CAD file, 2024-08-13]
Mechanical Design CAD Files/STEP Files/NNP-MAT-150-017-000 150 Micron Aluminum Oxide.STEP
16.0 x 7.01 x 0.0127 mm

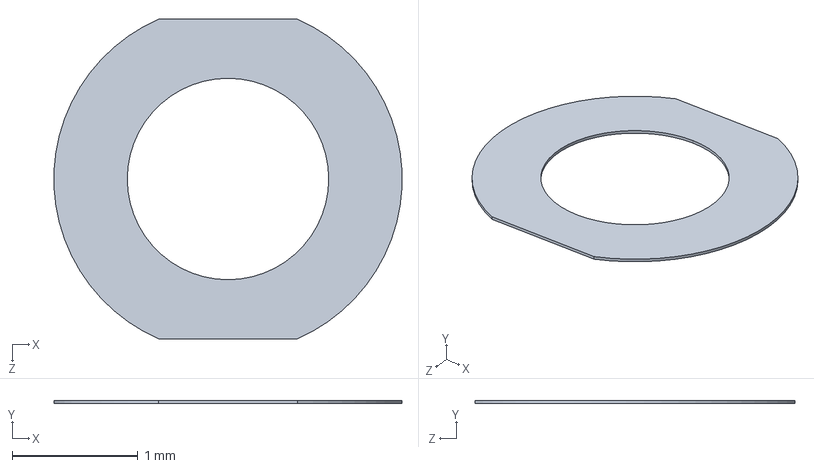
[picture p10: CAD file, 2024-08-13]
Mechanical Design CAD Files/STEP Files/NNP-DWG-130-006-000 Remote Module, Header, Gasket.STEP
2.77 x 0.0254 x 2.54 mm

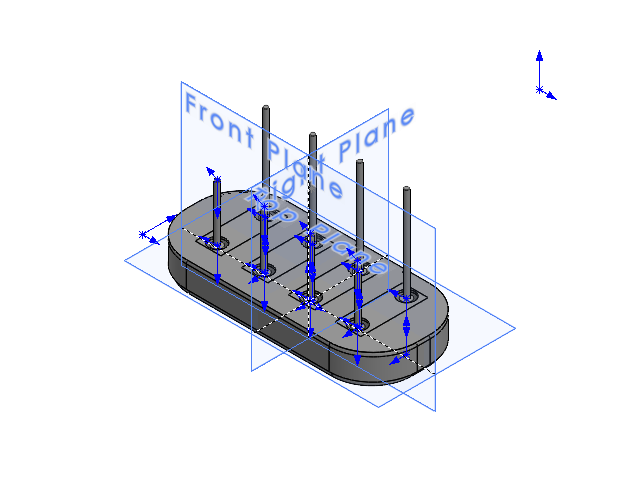
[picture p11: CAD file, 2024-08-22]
Mechanical Design CAD Files/SolidWorks Native Files/NNP-DWG-135-001-001 SA, Remote Module, Capthrough Sandblasted.SLDASM
NNP-DWG-130-010-000 Remote Module, Capthrough, Lid
NNP-DWG-130-008-000 Capthrough, Ceramic x 8
NNP-DWG-130-009-001 Capthrough, Pin, Ring x 4
NNP-DWG-130-009-002 Capthrough, Pin, Jogged x 4
NNP-MAT-150-017-000 150 Micron Aluminum Oxide
NNP-MAT-150-008-000 EPO-TEK 301

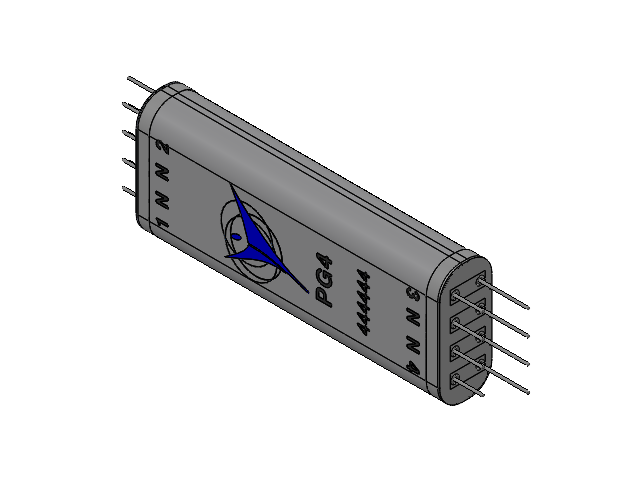
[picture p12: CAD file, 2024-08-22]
Mechanical Design CAD Files/SolidWorks Native Files/NNP-DWG-125-002-000 SA, PG4 Module, Weld Assembly.SLDASM
NNP-DWG-130-001-000 Remote Module, Case
NNP-DWG-125-001-000 Remote Module, PG4, Flexible Circuit Assembly
NNP-DWG-130-002-000 Remote Module, Insulator Flex x 2
NNP-DWG-130-010-000 Remote Module, Capthrough, Lid x 2
NNP-DWG-130-008-000 Capthrough, Ceramic x 16
NNP-DWG-130-009-001 Capthrough, Pin, Ring x 8
NNP-DWG-130-009-002 Capthrough, Pin, Jogged x 8
NNP-MAT-150-017-000 150 Micron Aluminum Oxide x 2
NNP-MAT-150-008-000 EPO-TEK 301 x 2
NNP-MAT-150-006-000 70% Isopropyl Alochol x 2
NNP-MAT-150-005-000 Distilled Water

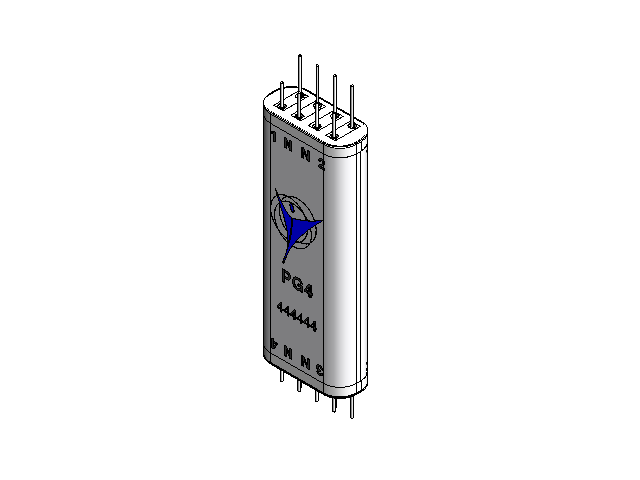
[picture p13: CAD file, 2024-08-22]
Mechanical Design CAD Files/SolidWorks Native Files/NNP-DWG-125-002-001 SA, PG4 Module, Tack Weld Assembly.SLDASM
NNP-DWG-130-001-000 Remote Module, Case
NNP-DWG-125-001-000 Remote Module, PG4, Flexible Circuit Assembly
NNP-DWG-130-002-000 Remote Module, Insulator Flex x 2
NNP-DWG-130-010-000 Remote Module, Capthrough, Lid x 2
NNP-DWG-130-008-000 Capthrough, Ceramic x 16
NNP-DWG-130-009-001 Capthrough, Pin, Ring x 8
NNP-DWG-130-009-002 Capthrough, Pin, Jogged x 8
NNP-MAT-150-017-000 150 Micron Aluminum Oxide x 2
NNP-MAT-150-008-000 EPO-TEK 301 x 2
NNP-MAT-150-006-000 70% Isopropyl Alochol x 2
NNP-MAT-150-005-000 Distilled Water

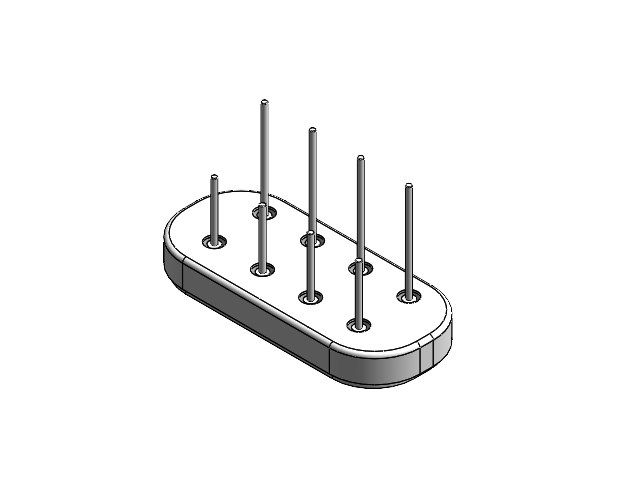
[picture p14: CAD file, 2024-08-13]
Mechanical Design CAD Files/SolidWorks Native Files/NNP-DWG-135-001-000 SA, Remote Module, Capthrough.SLDASM
NNP-DWG-130-010-000 Remote Module, Capthrough, Lid
NNP-DWG-130-008-000 Capthrough, Ceramic x 8
NNP-DWG-130-009-001 Capthrough, Pin, Ring x 4
NNP-DWG-130-009-002 Capthrough, Pin, Jogged x 4

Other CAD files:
Mechanical Design CAD Files/SolidWorks Native Files/NNP-DWG-130-001-000 Remote Module, Case.SLDPRT
Mechanical Design CAD Files/STEP Files/NNP-DWG-130-001-000 Remote Module, Case, No Marking.STEP
Mechanical Design CAD Files/SolidWorks Native Files/NNP-DWG-130-008-000 Capthrough, Ceramic.SLDPRT
Mechanical Design CAD Files/STEP Files/NNP-DWG-120-001-000 Remote Module, Case, PG4 Marking.STEP
Mechanical Design CAD Files/STEP Files/NNP-DWG-130-001-000 Remote Module, Case.STEP
Mechanical Design CAD Files/STEP Files/NNP-DWG-130-002-000 Remote Module, Insulator Flex.STEP
Mechanical Design CAD Files/STEP Files/NNP-DWG-130-003-000 Remote Module, Pre-Molded Header Body.STEP
Mechanical Design CAD Files/STEP Files/NNP-DWG-130-004-000 Remote Module, Pre-Molded Header Cap.STEP
Mechanical Design CAD Files/STEP Files/NNP-DWG-130-007-000 Remote Module, Suture Skirt.STEP
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

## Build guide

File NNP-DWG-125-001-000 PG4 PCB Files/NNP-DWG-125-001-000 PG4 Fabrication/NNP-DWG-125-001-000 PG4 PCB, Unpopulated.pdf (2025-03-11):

D | D
1. Board Technology
A. The Rigid-Flexible PCB shall be fabricated to IPC-6013 Types 1 to 3 and 5, Class 3
and IPC-2223 Types 1 to 3 and 5, Class 3 standards.
B. Maximum overall rigid thickness shall not exceed 450um. This is measured over
finished plated surfaces. The maximum overall flexible thickness shall not exceed 120.0um
C. Finished hole size unless noted should be +/- 3 mil (0.076mm)
D. All materials must be compliant with the European Union RoHS 2 directive, 2011/65/EU
E. Finish shall be ENIG
1. Electroless nickel thickness: 3-6um (Refer to IPC-4552)
2 Immersion Gold Thickness: .051-0.127um (refer to IPC-4552)
F. Solder mask shall be LPI, Blue, 15-25um thick, and on both sides.
G. No silkscreen on either side.
2. Certificate of Conformity:
A. Complete description of the item with revision
B. Number of lot and Date Code

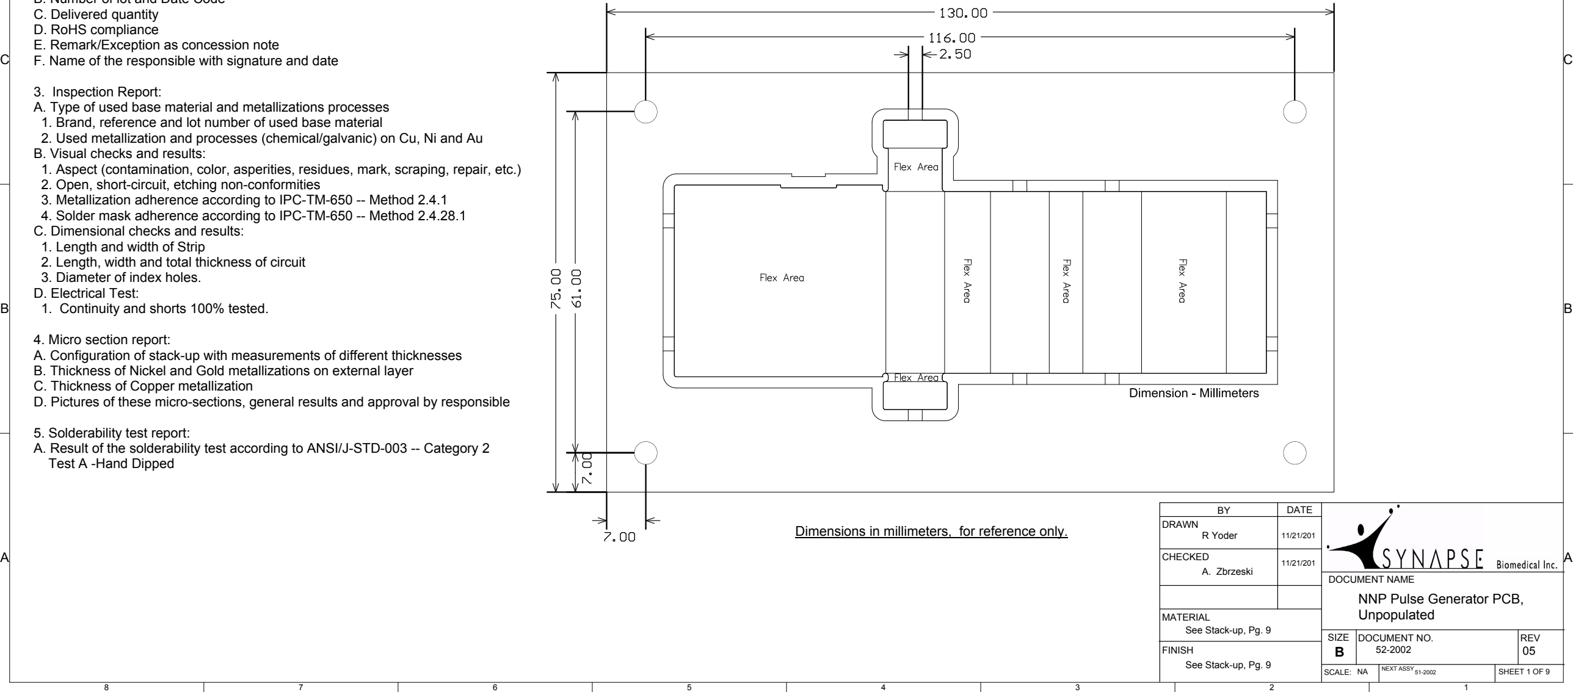
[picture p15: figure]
C. Delivered quantity D. RoHS compliance E. Remark/Exception as concession note; 3. Inspection Report:; B. Visual checks and results:; C. Dimensional checks and results: 1. Length and width of Strip; 3. Diameter of index holes. D. Electrical Test: 1. Continuity and shorts 100% tested.; 4. Micro section report:; C. Thickness of Copper metallization; 5. Solderability test report:; Test A -Hand Dipped; CHECKED A. Zbrzeski; DRAWN R Yoder; NNP Pulse Generator PCB, Unpopulated; DOCUMENT NAME; DOCUMENT NO.; REV; NEXT ASSY; SCALE:; SIZE; FINISH; MATERIAL; DATE; SHEET 1 OF 9; See Stack-up, Pg. 9

F. Name of the responsible with signature and date
A. Type of used base material and metallizations processes
1. Brand, reference and lot number of used base material
2. Used metallization and processes (chemical/galvanic) on Cu, Ni and Au
1. Aspect (contamination, color, asperities, residues, mark, scraping, repair, etc.)
2. Open, short-circuit, etching non-conformities
3. Metallization adherence according to IPC-TM-650 -- Method 2.4.1
4. Solder mask adherence according to IPC-TM-650 -- Method 2.4.28.1
2. Length, width and total thickness of circuit
A. Configuration of stack-up with measurements of different thicknesses
B. Thickness of Nickel and Gold metallizations on external layer
D. Pictures of these micro-sections, general results and approval by responsible
A. Result of the solderability test according to ANSI/J-STD-003 -- Category 2
ECN | REV | DESCRIPTION
DCN-105 --- | 01 | Initial Release, Never Built by SBI
| 02 | Updated manufacture notes.Never released
| 03
- Updated manufacture notes and Layer Stack.
- Added Dummy Copper (Copper Pour) to Layer 3.
- Never Released

Dimensions in millimeters, for reference only.

DCN-108

04

- Changed VIA annular rings and drill sizes to meet IPC Class 3.
- Changed Drill Charts to matched drill files and Note 1D.
- Changed the copper pour on the rigid edge layer 4
to match the copper pour on layer 2
- Changed Note 5A Soderability Test
- Deleted Note 6
- Added dummy copper on frame top and bottom layer.
- Mirror Board part number on bottom layer
- Updated Layer stack
- Removed Material description from manufacture notes.
- Changed text in Material and Finish blocks from "See Notes and Stack-up" to "See Stack-up, Pg. 9".

DCN-109 05

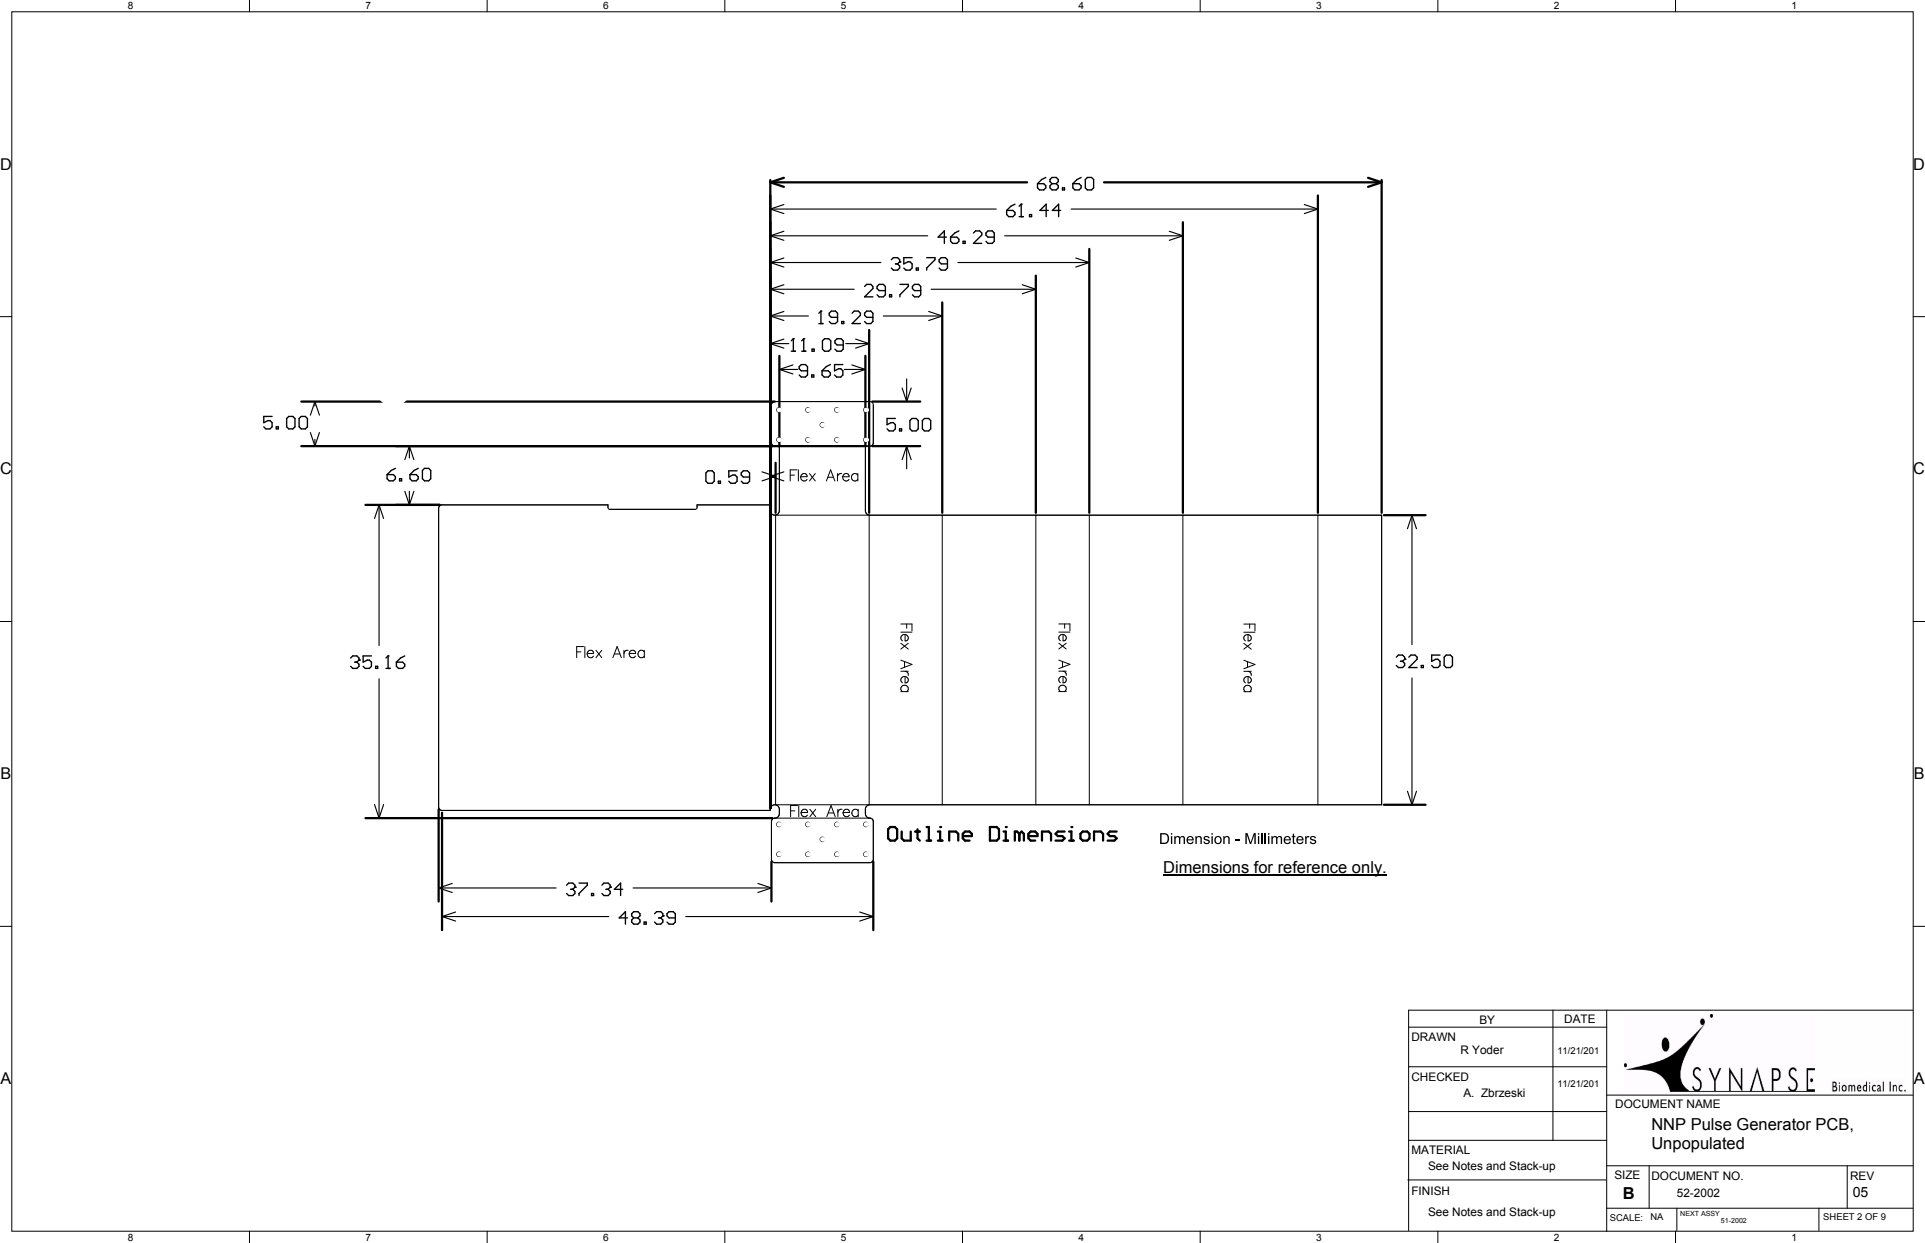
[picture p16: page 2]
DATE

Dimensions for reference only.

DRAWN R Yoder | 11/21/201

CHECKED A. Zbrzeski

DOCUMENT NAME
NNP Pulse Generator PCB,

See Notes and Stack-up

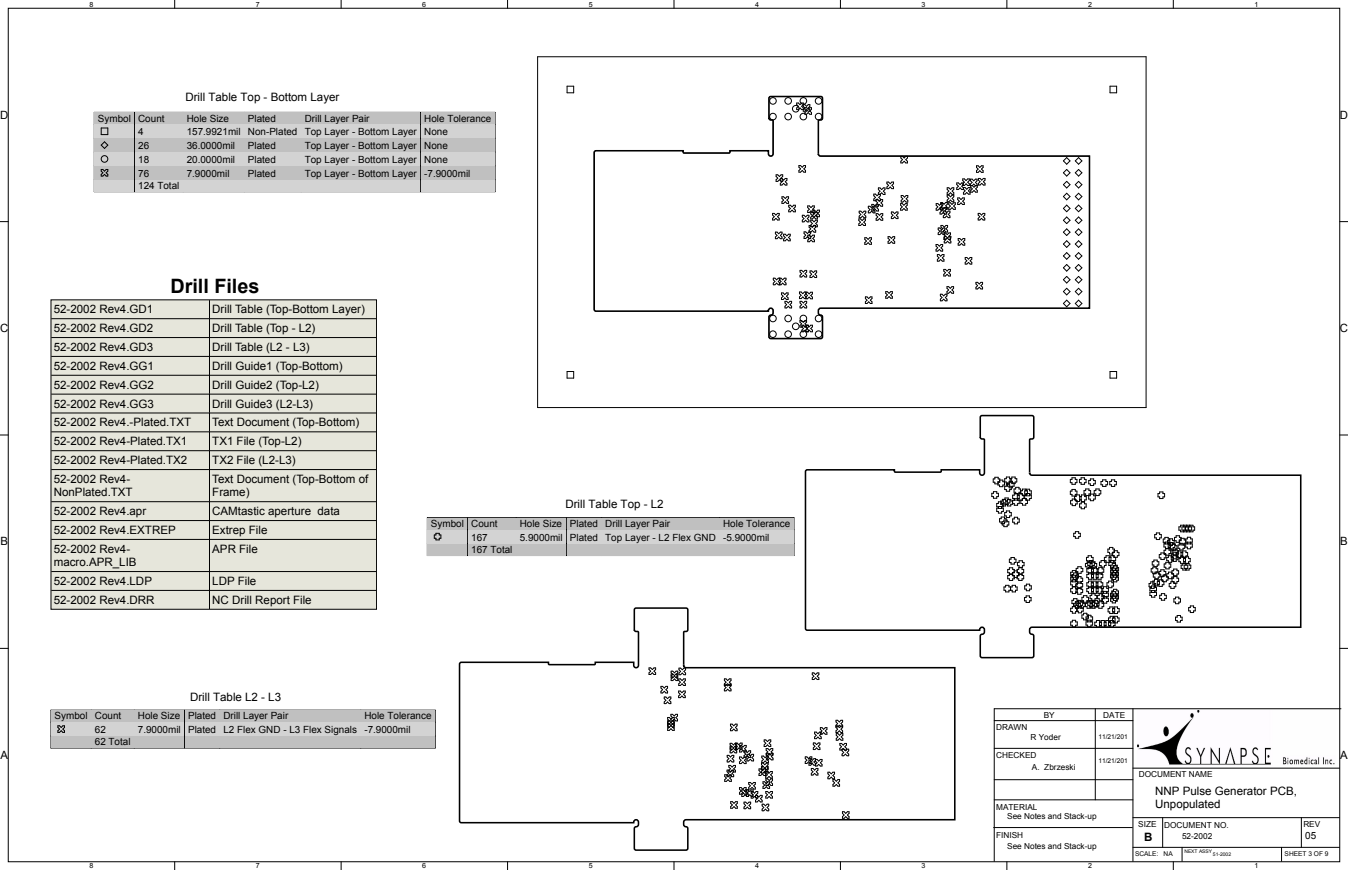
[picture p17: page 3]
R Yoder; DRAWN; DATE; Symbol; Count; Hole Size 7.9000mil; Plated Plated; Hole Tolerance -7.9000mil; Drill Table L2 - L3; 52-2002 Rev4.GD1; Drill Table (Top-Bottom Layer); 52-2002 Rev4.GD2; Drill Table (Top - L2); 52-2002 Rev4.GD3; Drill Table (L2 - L3); 52-2002 Rev4.GG1; Drill Guide1 (Top-Bottom); 52-2002 Rev4.GG2; Drill Guide2 (Top-L2); 52-2002 Rev4.GG3; Drill Guide3 (L2-L3); 52-2002 Rev4.-Plated.TXT; Text Document (Top-Bottom); 52-2002 Rev4-Plated.TX1; TX1 File (Top-L2)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

Drill Table Top - Bottom Layer

Symbol | Count | Hole Size | Plated | Drill Layer Pair | Hole Tolerance

4 | 157.9921mil | Non-Plated | Top Layer - Bottom Layer | None
26 | 36.0000mil | Plated | Top Layer - Bottom Layer | None
18 | 20.0000mil | Plated | Top Layer - Bottom Layer | None
76 | 7.9000mil | Plated | Top Layer - Bottom Layer | -7.9000mil
124 Total

Text Document (Top-Bottom of
Frame)

Drill Table Top - L2

167 | 5.9000mil | Plated | Top Layer - L2 Flex GND | -5.9000mil
167 Total

Drill Layer Pair
L2 Flex GND - L3 Flex Signals

62 Total

CHECKED A. Zbrzeski | 11/21/201

DOCUMENT NAME
NNP Pulse Generator PCB,

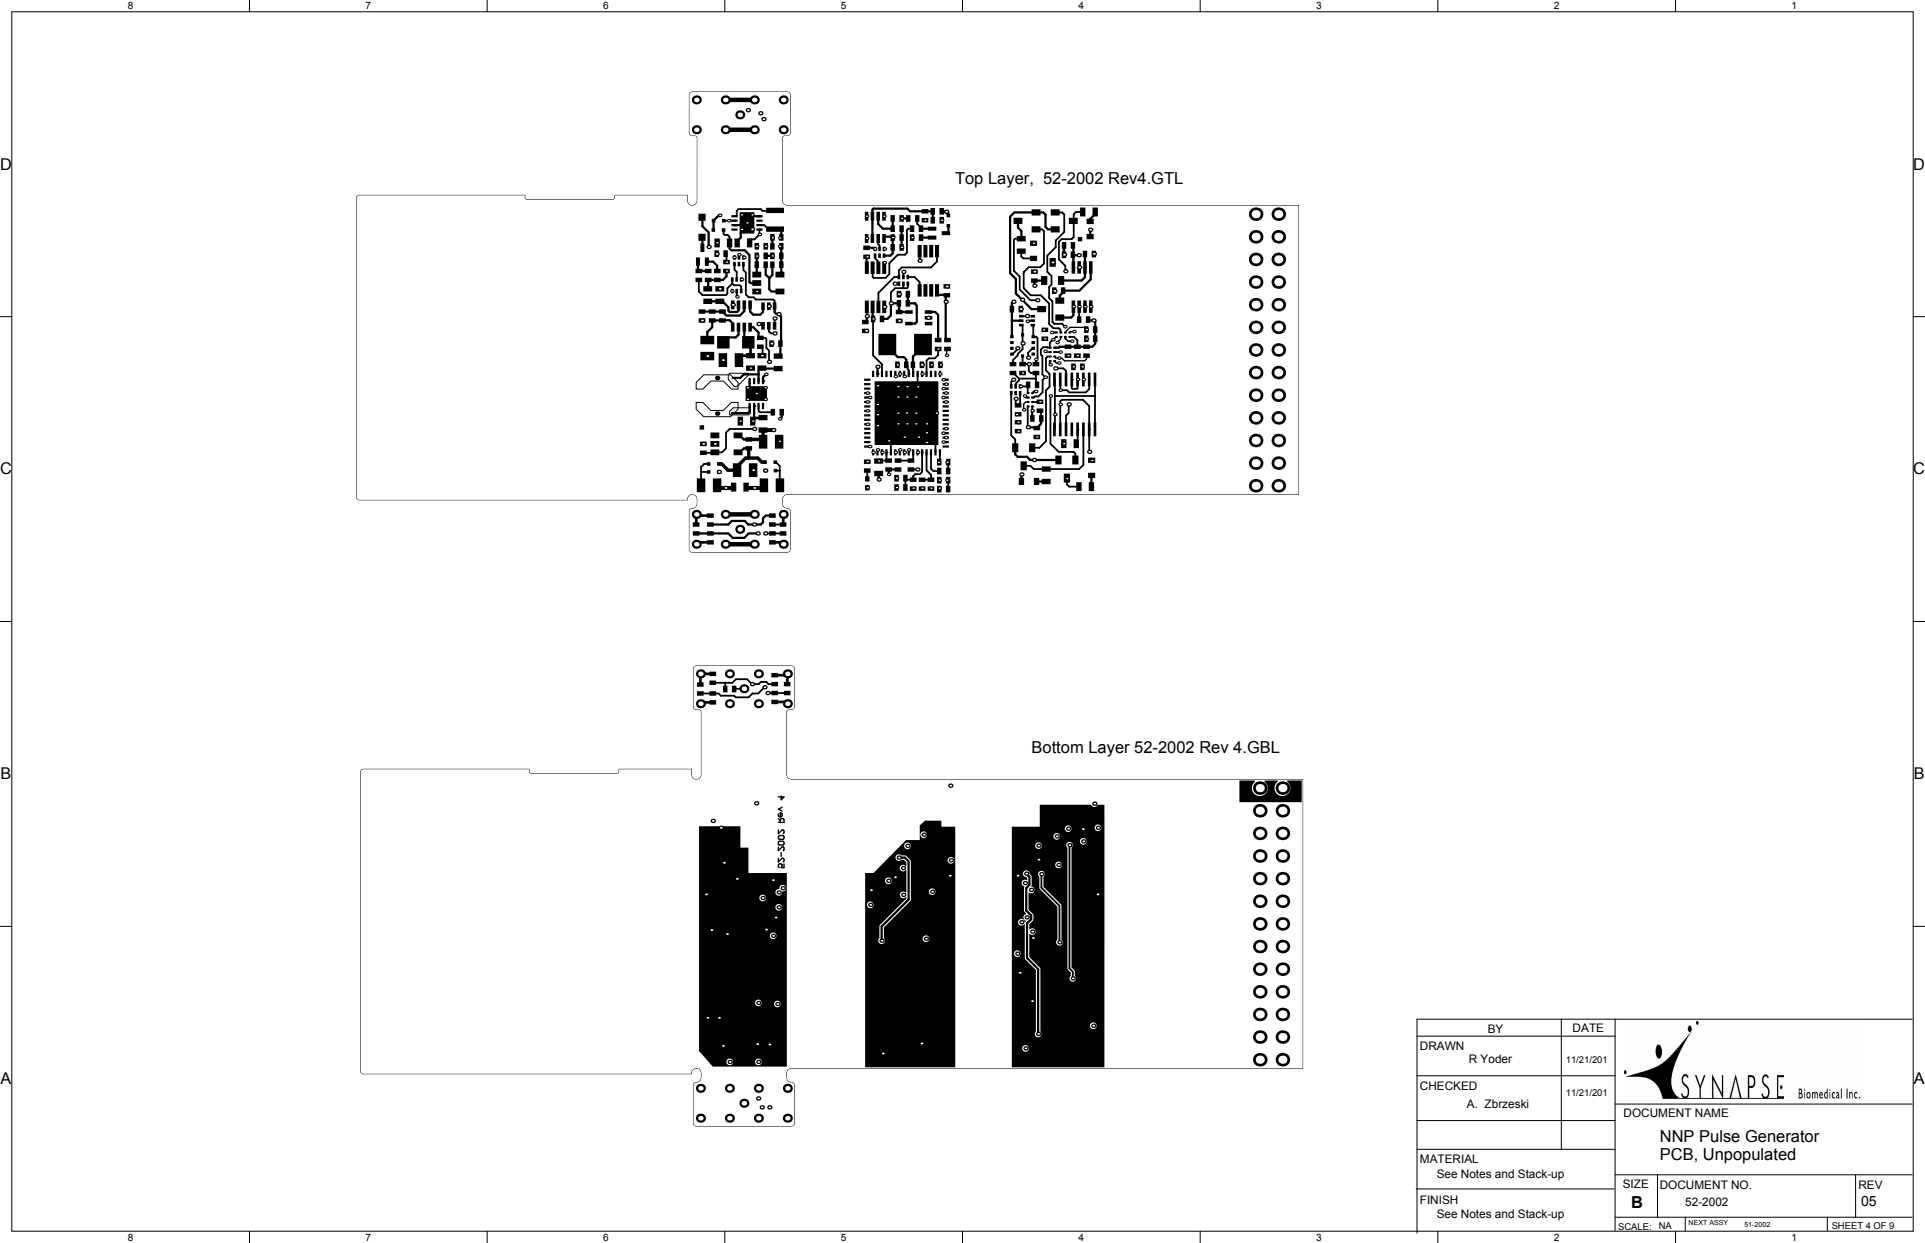
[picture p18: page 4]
DATE

Top Layer, 52-2002 Rev4.GTL

Bottom Layer 52-2002 Rev 4.GBL

DRAWN R Yoder | 11/21/201

CHECKED A. Zbrzeski | 11/21/201

DOCUMENT NAME
NNP Pulse Generator
PCB, Unpopulated

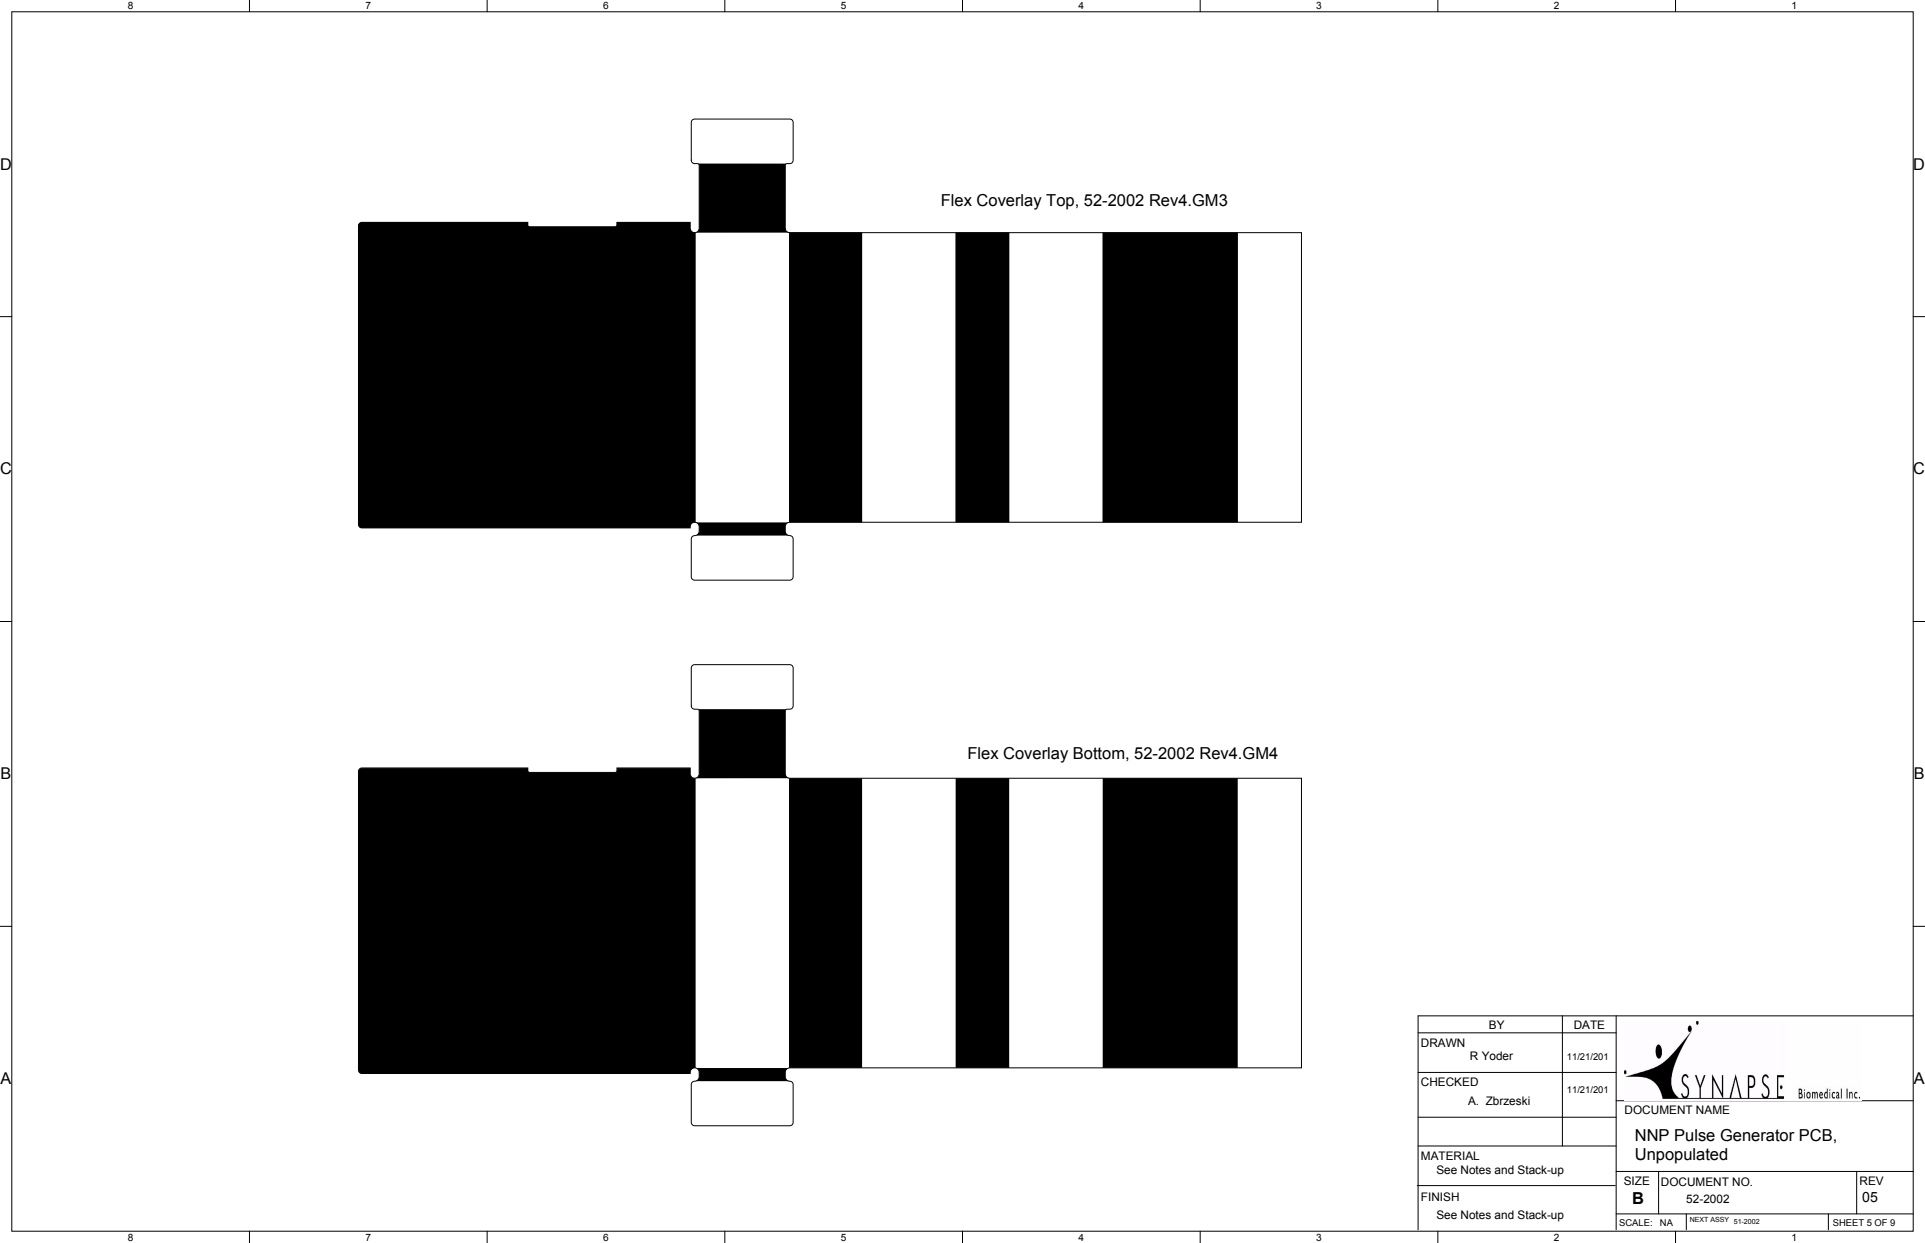
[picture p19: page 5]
DATE

Flex Coverlay Top, 52-2002 Rev4.GM3

Flex Coverlay Bottom, 52-2002 Rev4.GM4

DRAWN R Yoder | 11/21/201

CHECKED A. Zbrzeski | 11/21/201

DOCUMENT NAME
NNP Pulse Generator PCB,

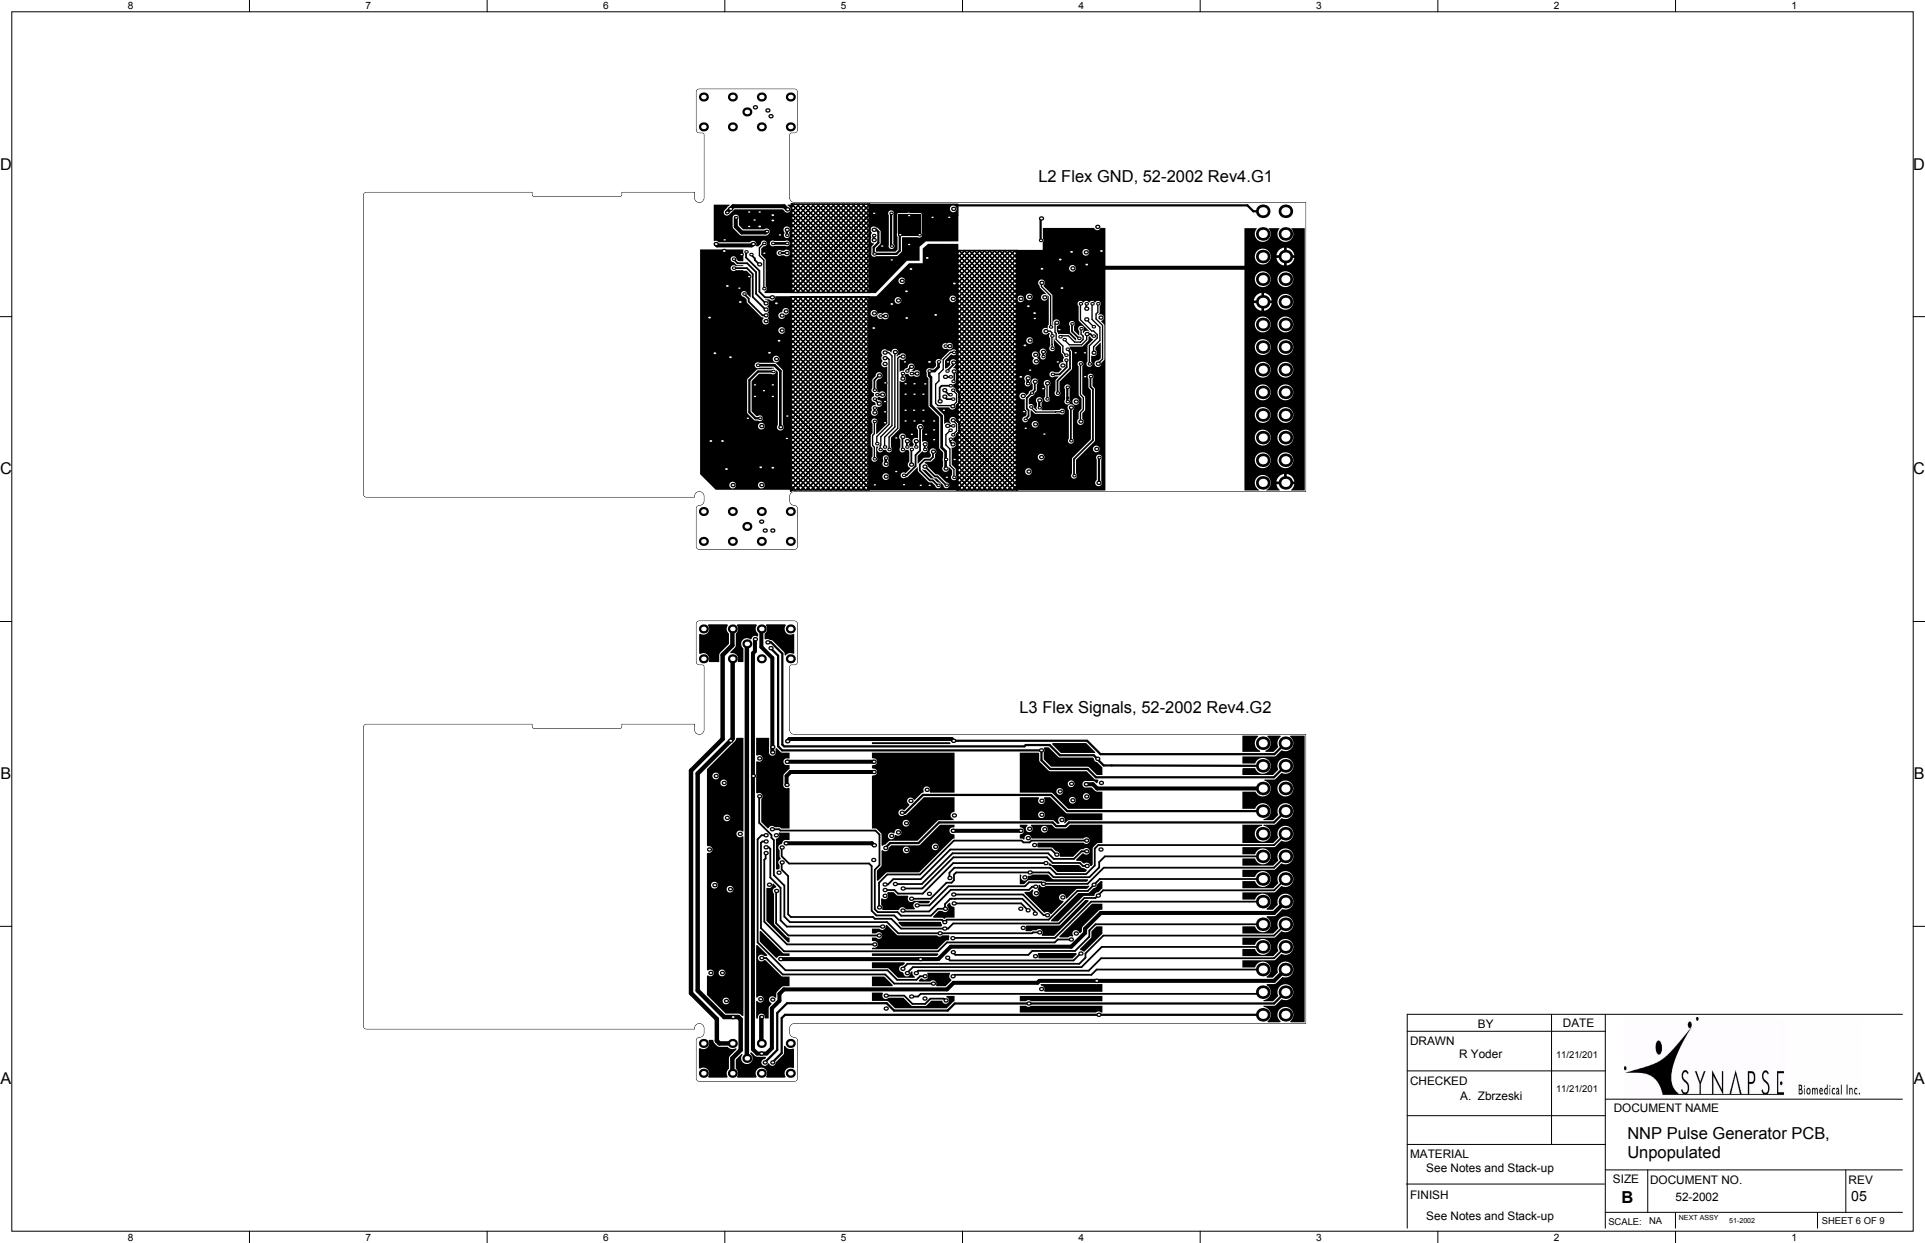
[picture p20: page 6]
L3 Flex Signals, 52-2002 Rev4.G2; L2 Flex GND, 52-2002 Rev4.G1; DATE; See Notes and Stack-up

DRAWN R Yoder | 11/21/201

CHECKED A. Zbrzeski | 11/21/201

DOCUMENT NAME
NNP Pulse Generator PCB,

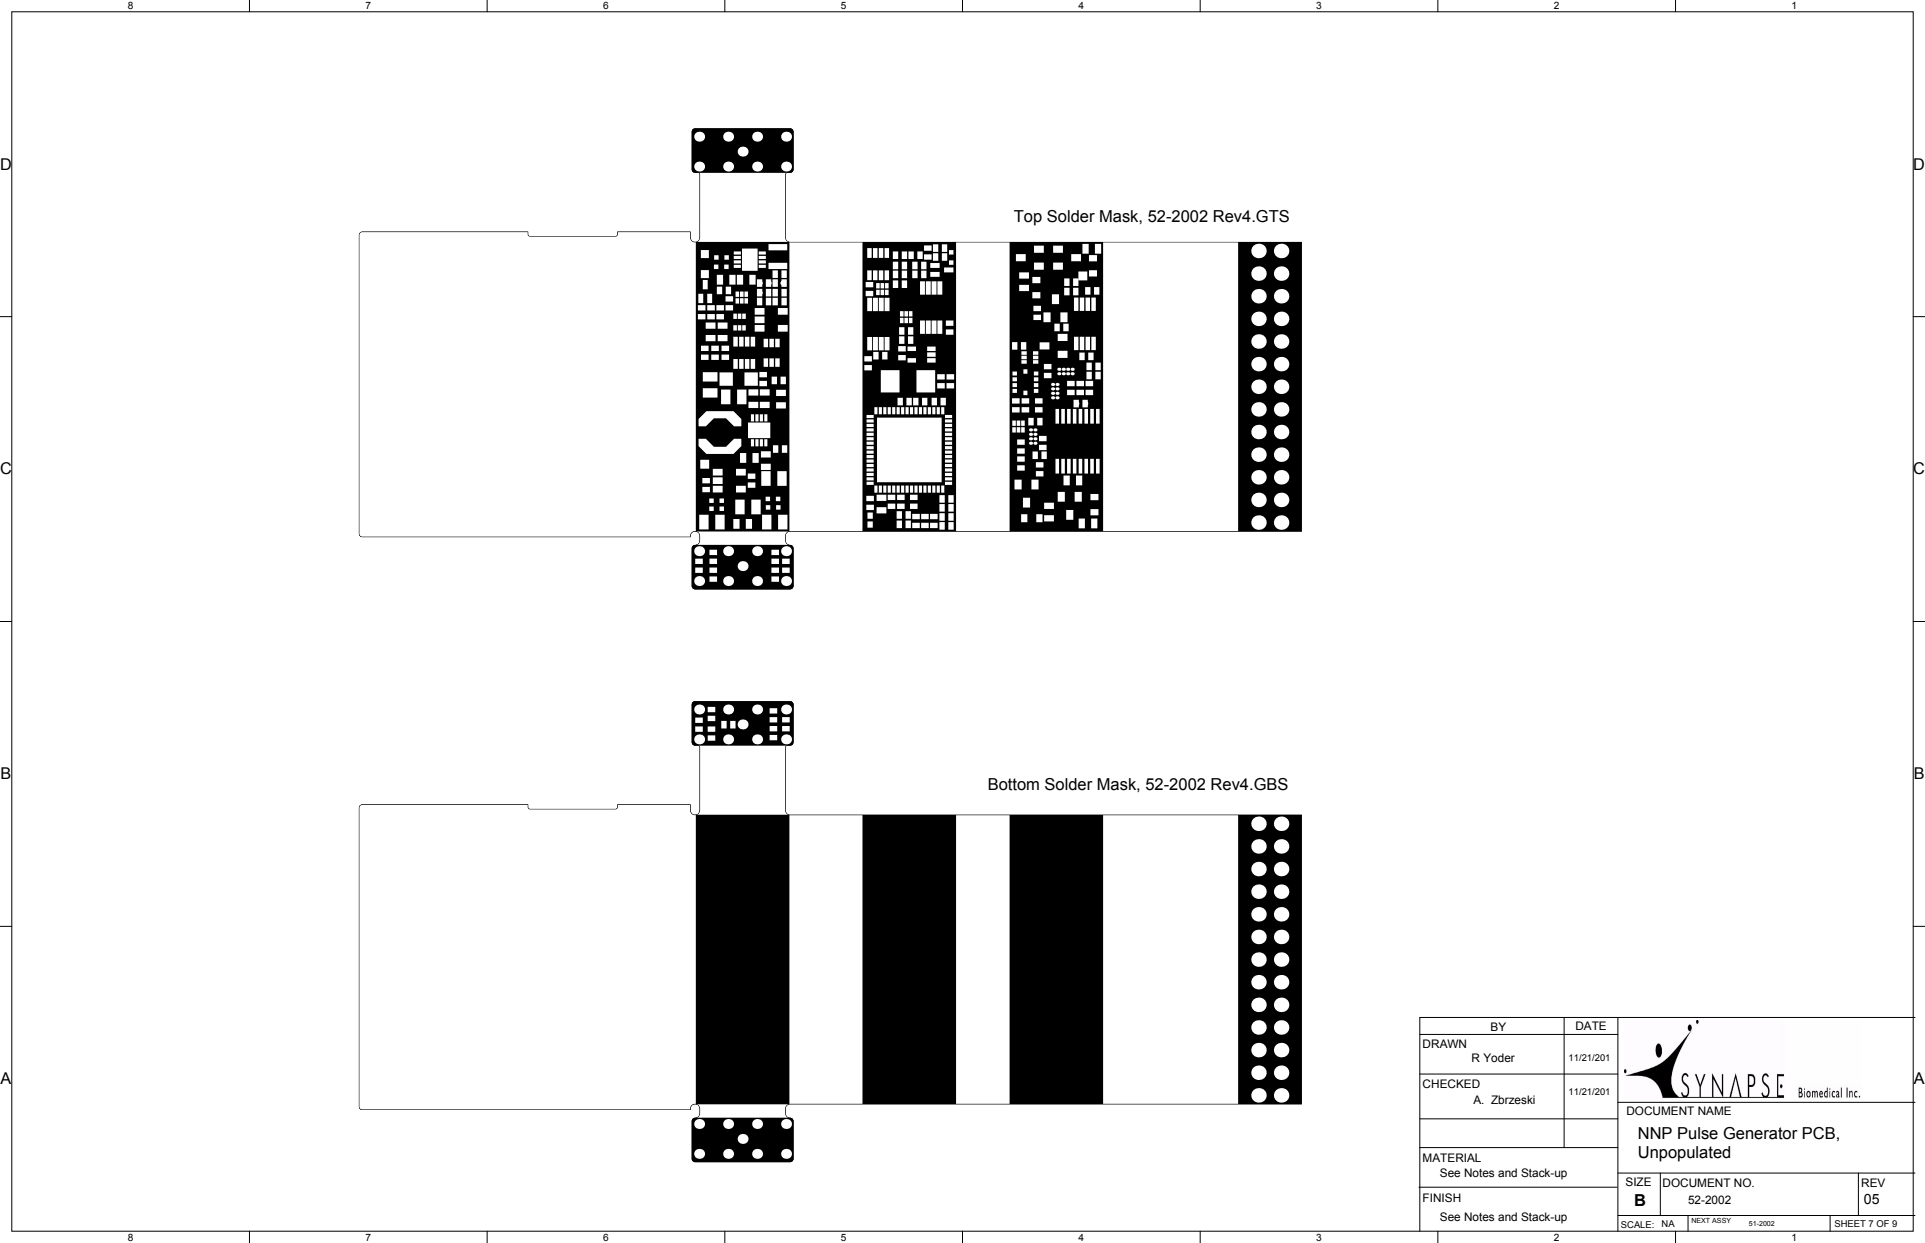
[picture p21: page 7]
DATE

Top Solder Mask, 52-2002 Rev4.GTS

Bottom Solder Mask, 52-2002 Rev4.GBS

DRAWN R Yoder | 11/21/201

CHECKED A. Zbrzeski | 11/21/201

DOCUMENT NAME
NNP Pulse Generator PCB,

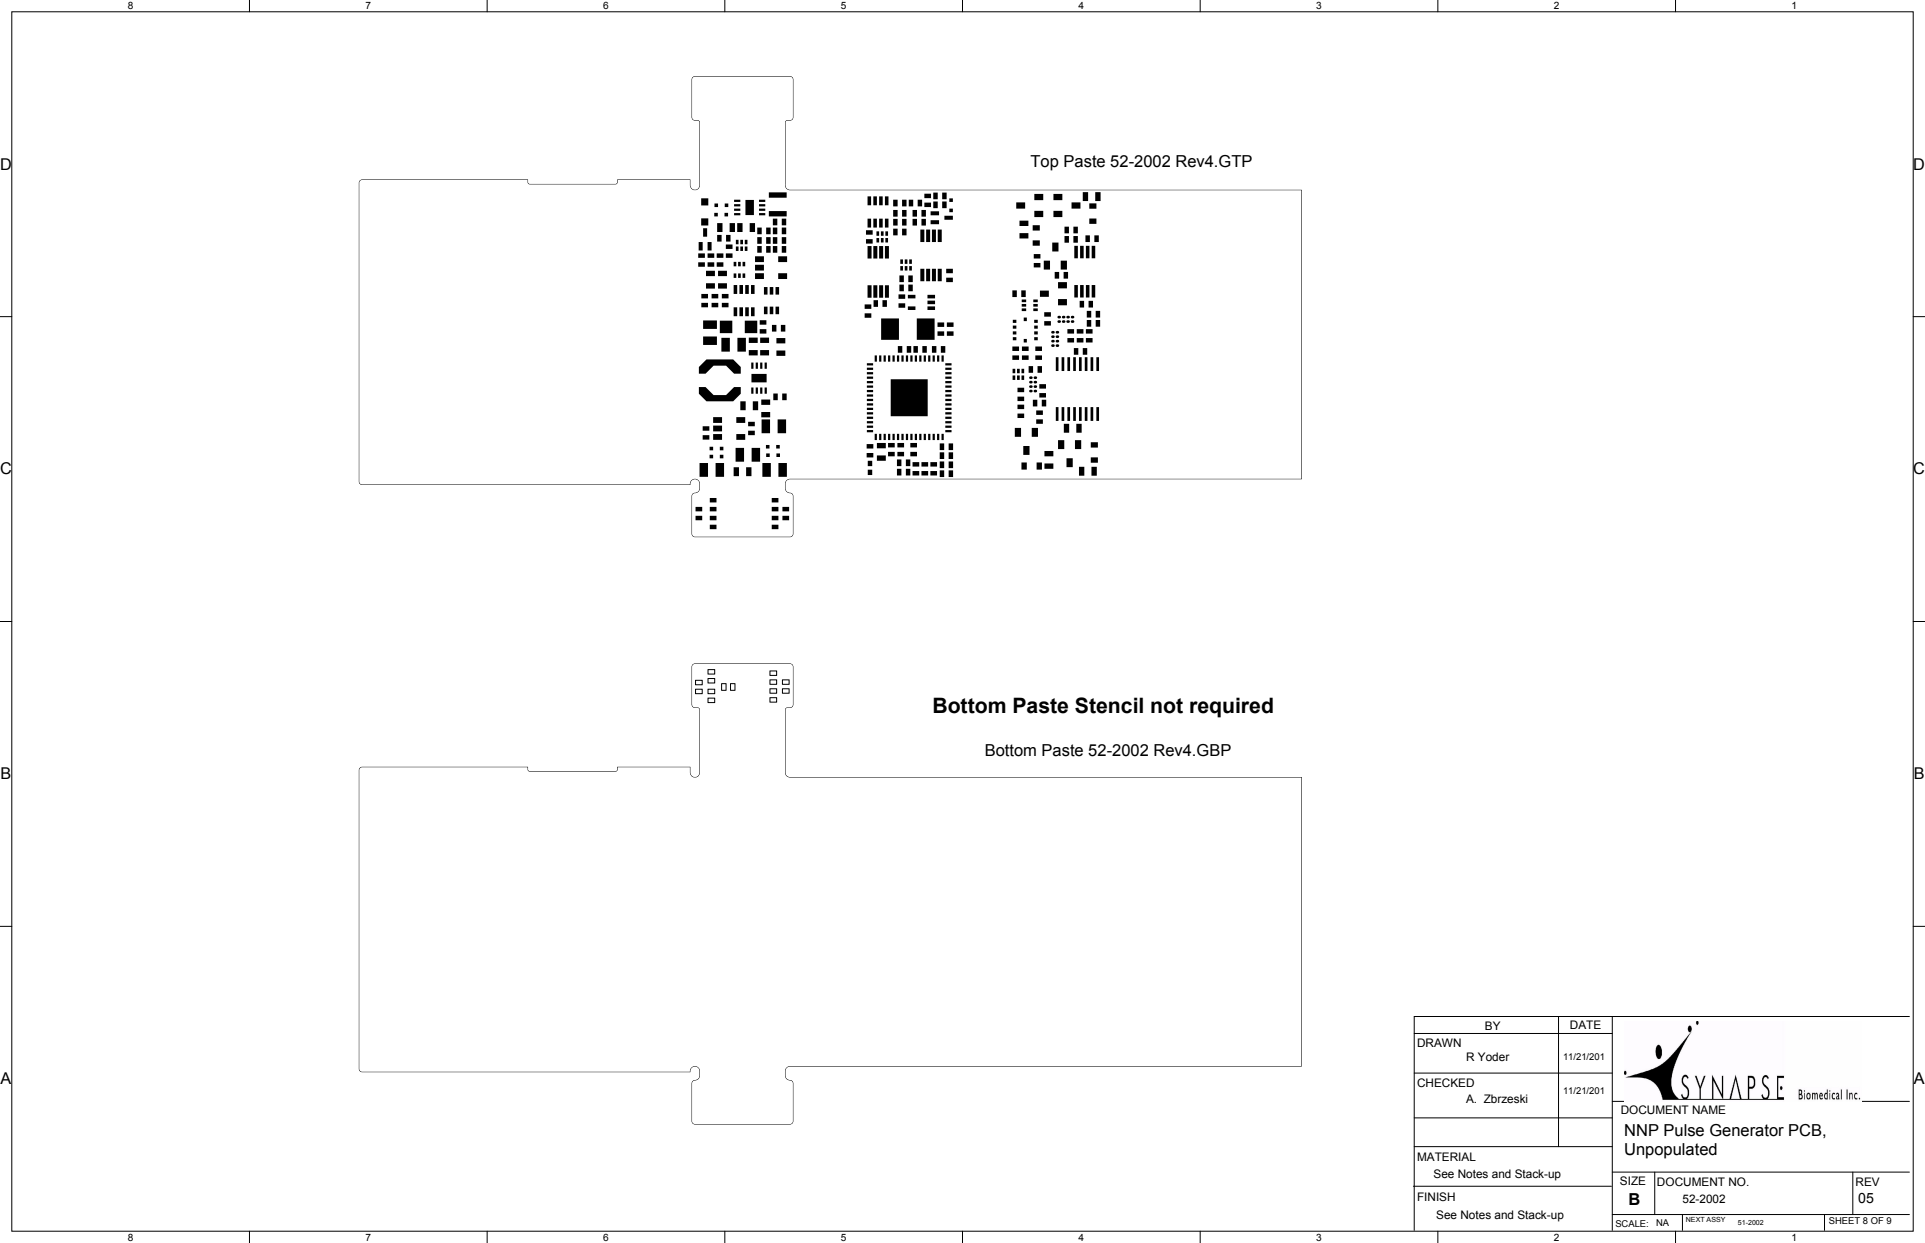
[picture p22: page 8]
DATE; SCALE:; SHEET 8 OF 9

Top Paste 52-2002 Rev4.GTP

Bottom Paste Stencil not required

Bottom Paste 52-2002 Rev4.GBP

DRAWN R Yoder | 11/21/201

CHECKED A. Zbrzeski | 11/21/201

DOCUMENT NAME
NNP Pulse Generator PCB,

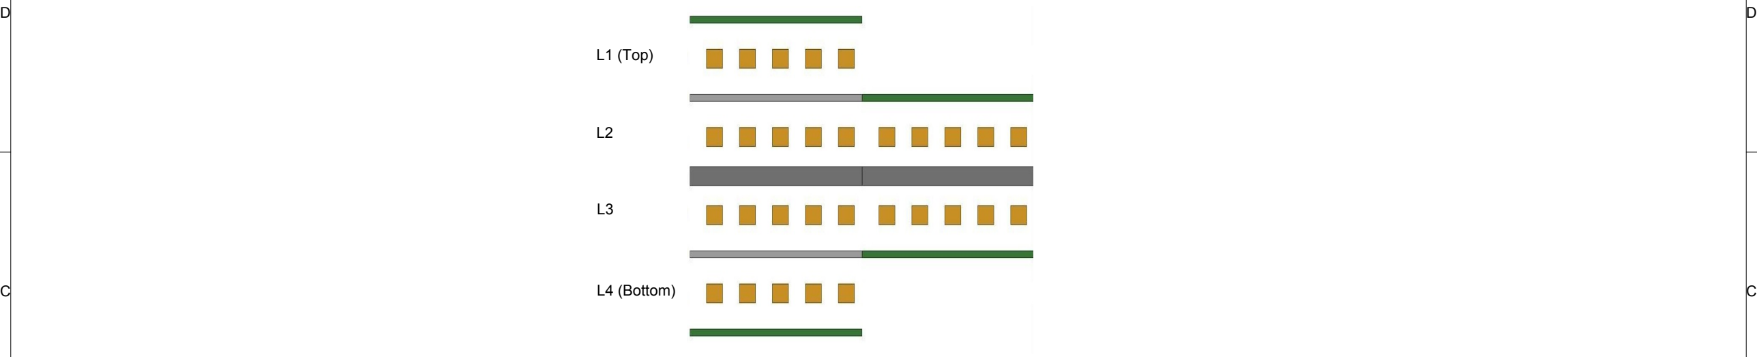
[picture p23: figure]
L1 (Top); L4 (Bottom)

B | B
A | A
BY | DATE
DRAWN R Yoder | 11/21/201
CHECKED A. Zbrzeski | 11/21/201

DOCUMENT NAME
NNP Pulse Generator PCB,
Rigid Area | Flex Area
Rigid Area | Flex Area
Layer 1, 0.7mil Cu base (0.5 oz), Copper
Dielectric, 2.0mil, VT-47 FR4 .002 H/0
Dielectric, 1.9mil, Prepreg 106 FR406 N.F. | Flex Coverlay Top, LF-7001, GM3
Layer 2, 0.7mil (0.5 oz), Copper, G1 | Layer 2, 0.7mil (0.5 oz), Copper, G1
Dielectric (Core), 1.0mil, Polyimide AP-8515R | Dielectric (Core), 1.0mil, Polyimide AP-8515R
Layer 3, 0.7mil (0.5 oz), Copper, G2 | Layer 3, 0.7mil (0.5 oz), Copper, G2
Dielectric, 1.9mil, Prepreg 106 FR406 N.F. | Flex Coverlay Bottom, LF-7001, GM4
Dielectric, 2.0mil, VT-47 FR4 .002 H/0
Layer 4, 0.7mil Cu base (0.5 oz), Copper

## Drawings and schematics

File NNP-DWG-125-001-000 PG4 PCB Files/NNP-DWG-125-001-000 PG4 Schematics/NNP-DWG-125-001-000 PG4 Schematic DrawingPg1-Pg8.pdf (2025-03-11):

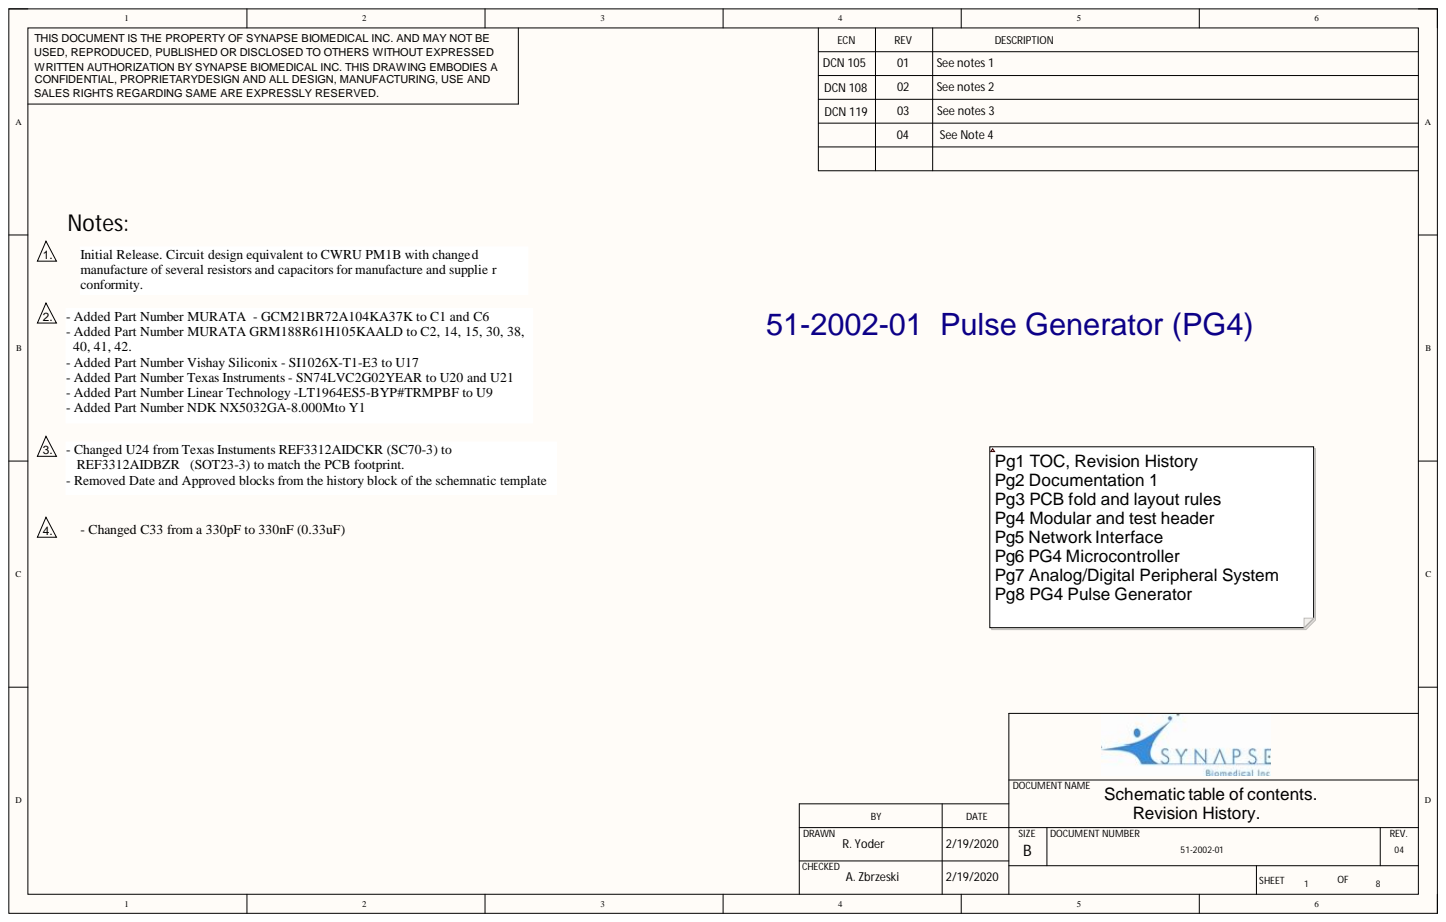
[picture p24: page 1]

THIS DOCUMENT IS THE PROPERTY OF SYNAPSE BIOMEDICAL INC. AND MAY NOT BE USED, REPRODUCED, PUBLISHED OR DISCLOSED TO OTHERS WITHOUT EXPRESSED WRITTEN AUTHORIZATION BY SYNAPSE BIOMEDICAL INC. THIS DRAWING EMBODIES A CONFIDENTIAL, PROPRIETARYDESIGN AND ALL DESIGN, MANUFACTURING, USE AND SALES RIGHTS REGARDING SAME ARE EXPRESSLY RESERVED. | | ECN | REV | DESCRIPTION

DCN 105 | 01 | See notes 1

DCN 108 | 02 | See notes 2

DCN 119 | 03 | See notes 3

04 | See Note 4

Initial Release. Circuit design equivalent to CWRU PM1B with changed
manufacture of several resistors and capacitors for manufacture and supplier
conformity.

- Added Part Number MURATA - GCM21BR72A104KA37K to C1 and C6
- Added Part Number MURATA GRM188R61H105KAALD to C2, 14, 15, 30, 38,
- Added Part Number Vishay Siliconix - SI1026X-T1-E3 to U17
- Added Part Number Texas Instruments - SN74LVC2G02YEAR to U20 and U21
- Added Part Number Linear Technology -LT1964ES5-BYP#TRMPBF to U9
- Added Part Number NDK NX5032GA-8.000Mto Y1

- Changed U24 from Texas Instuments REF3312AIDCKR (SC70-3) to
REF3312AIDBZR (SOT23-3) to match the PCB footprint.
- Removed Date and Approved blocks from the history block of the schemnatic template

Pg1 TOC, Revision History
Pg2 Documentation 1
Pg3 PCB fold and layout rules
Pg4 Modular and test header
Pg5 Network Interface
Pg6 PG4 Microcontroller
Pg7 Analog/Digital Peripheral System
Pg8 PG4 Pulse Generator

Schematic table of contents.
Revision History.

BY | DATE

DRAWN R. Yoder | 2/19/2020 | SIZE B | DOCUMENT NUMBER 51-2002-01 | REV. 04

CHECKED A. Zbrzeski | 2/19/2020 | | SHEET OF 1 8

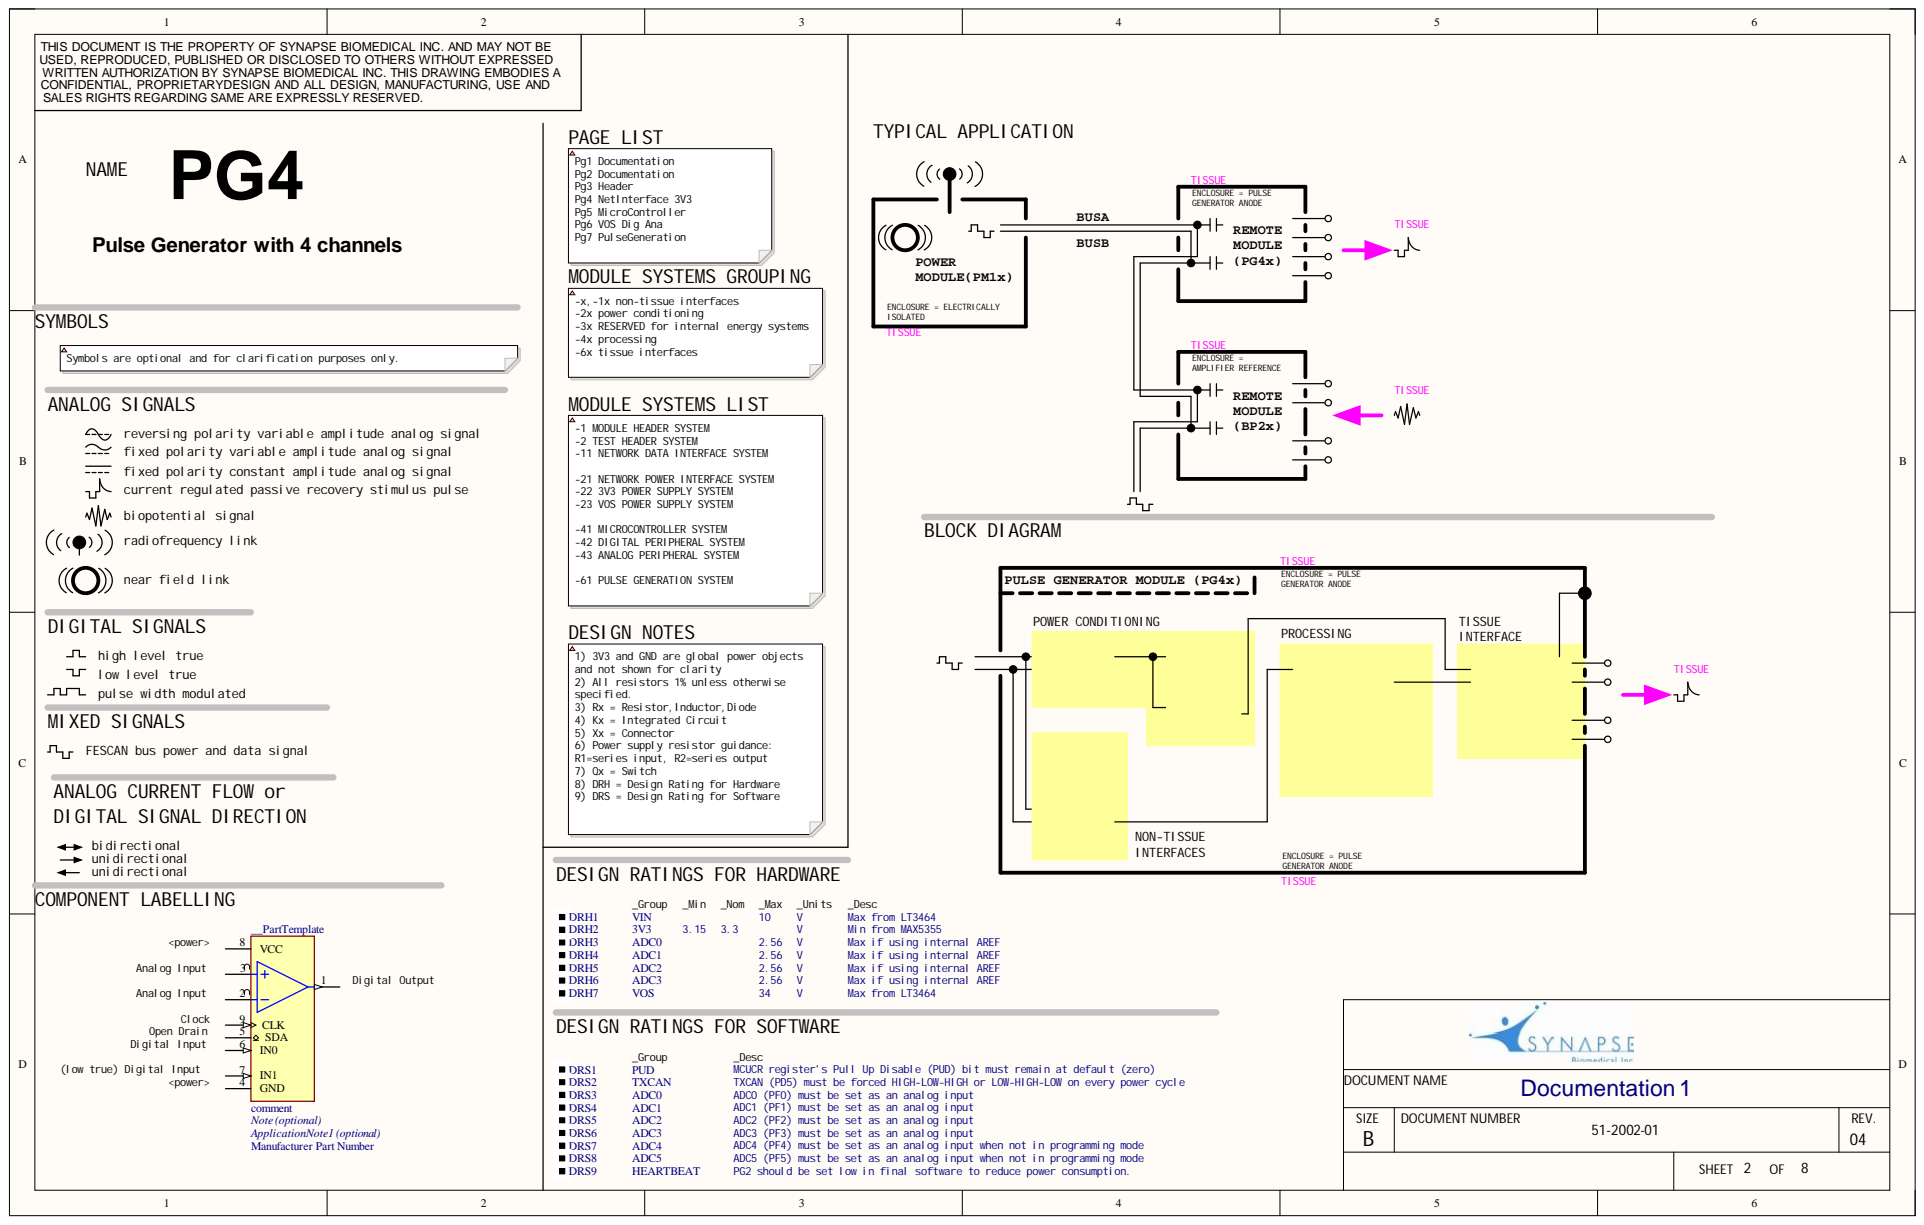
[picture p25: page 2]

THIS DOCUMENT IS THE PROPERTY OF SYNAPSE BIOMEDICAL INC. AND MAY NOT BE USED, REPRODUCED, PUBLISHED OR DISCLOSED TO OTHERS WITHOUT EXPRESSED WRITTEN AUTHORIZATION BY SYNAPSE BIOMEDICAL INC. THIS DRAWING EMBODIES A CONFIDENTIAL, PROPRIETARYDESIGN AND ALL DESIGN, MANUFACTURING, USE AND SALES RIGHTS REGARDING SAME ARE EXPRESSLY RESERVED. | | TYPICAL APPLICATION

Pulse Generator with 4 channels

-x,-1x non-tissue interfaces
-2x power conditioning
-3x RESERVED for internal energy systems
-4x processing
-6x tissue interfaces

Symbols are optional and for clarification purposes only.

reversing polarity variable amplitude analog signal
fixed polarity variable amplitude analog signal
fixed polarity constant amplitude analog signal
current regulated passive recovery stimulus pulse

-1 MODULE HEADER SYSTEM
-2 TEST HEADER SYSTEM
-11 NETWORK DATA INTERFACE SYSTEM

-21 NETWORK POWER INTERFACE SYSTEM
-22 3V3 POWER SUPPLY SYSTEM
-23 VOS POWER SUPPLY SYSTEM

1) 3V3 and GND are global power objects
and not shown for clarity
2) All resistors 1% unless otherwise
specified.
3) Rx = Resistor,Inductor,Diode
4) Kx = Integrated Circuit
5) Xx = Connector
6) Power supply resistor guidance:
R1=series input, R2=series output
7) Qx = Switch
8) DRH = Design Rating for Hardware
9) DRS = Design Rating for Software

FESCAN bus power and data signal

ANALOG CURRENT FLOW or
DIGITAL SIGNAL DIRECTION

DESIGN RATINGS FOR HARDWARE

DESIGN RATINGS FOR SOFTWARE

SIZE B | DOCUMENT NUMBER | REV.

SHEET 2 OF 8

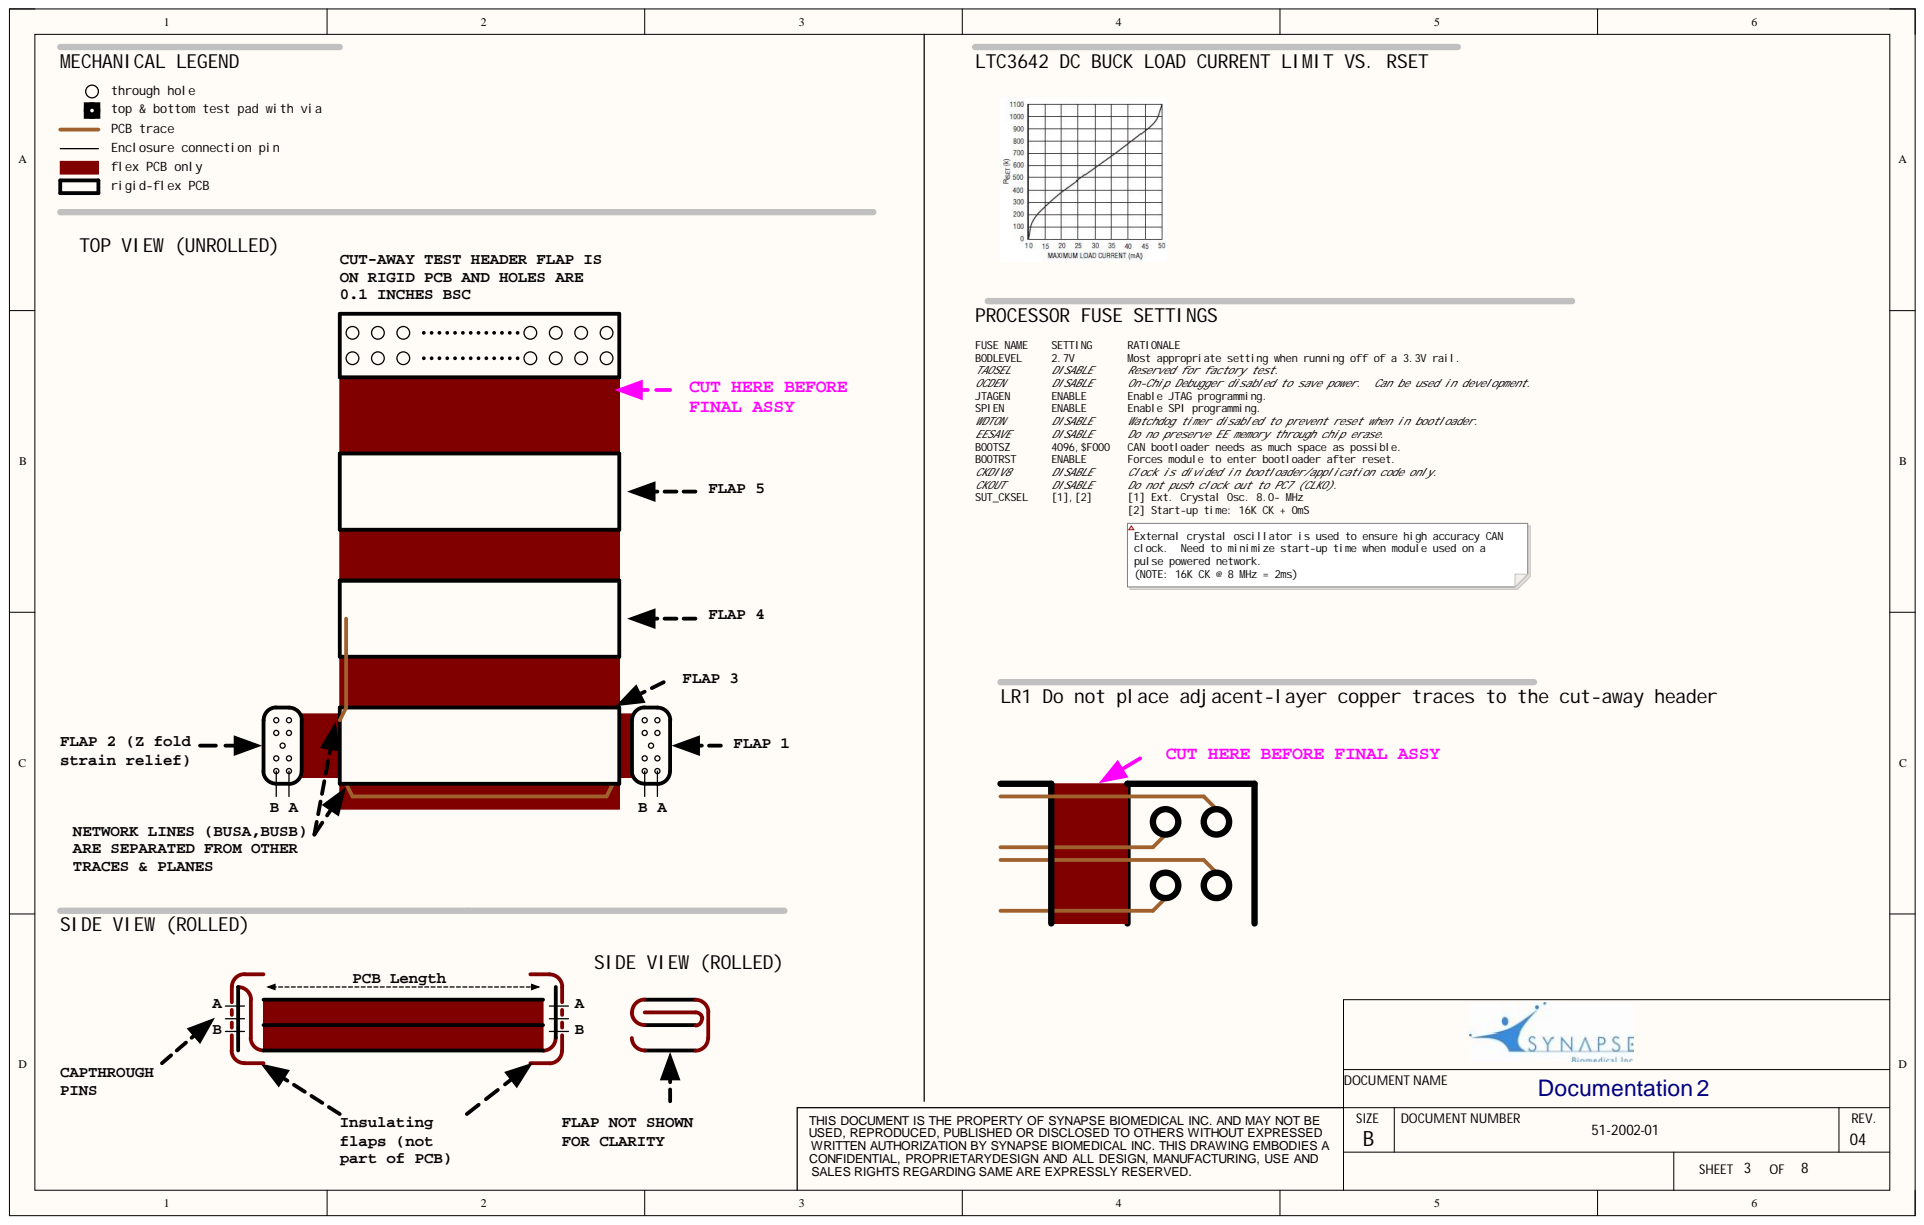
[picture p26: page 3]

LTC3642 DC BUCK LOAD CURRENT LIMIT VS. RSET

through hole
top & bottom test pad with via
PCB trace
Enclosure connection pin
flex PCB only
rigid-flex PCB

ON RIGID PCB AND HOLES ARE 0.1 INCHES BSC

RATIONALE
Most appropriate setting when running off of a 3.3V rail.
Reserved for factory test.
On-Chip Debugger disabled to save power. Can be used in development.
Enable JTAG programming.
Enable SPI programming.
Watchdog timer disabled to prevent reset when in bootloader.
Do no preserve EE memory through chip erase.
CAN bootloader needs as much space as possible.

[2] Start-up time: 16K CK + 0mS

External crystal oscillator is used to ensure high accuracy CAN
clock. Need to minimize start-up time when module used on a
pulse powered network.
(NOTE: 16K CK @ 8 MHz = 2ms)

LR1 Do not place adjacent-layer copper traces to the cut-away header

CUT HERE BEFORE FINAL ASSY

NETWORK LINES (BUSA,BUSB)
ARE SEPARATED FROM OTHER
TRACES & PLANES

THIS DOCUMENT IS THE PROPERTY OF SYNAPSE BIOMEDICAL INC. AND MAY NOT BE USED, REPRODUCED, PUBLISHED OR DISCLOSED TO OTHERS WITHOUT EXPRESSED WRITTEN AUTHORIZATION BY SYNAPSE BIOMEDICAL INC. THIS DRAWING EMBODIES A CONFIDENTIAL, PROPRIETARYDESIGN AND ALL DESIGN, MANUFACTURING, USE AND SALES RIGHTS REGARDING SAME ARE EXPRESSLY RESERVED. | SIZE B | DOCUMENT NUMBER | REV. 04 51-2002-01

SHEET 3 OF 8
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

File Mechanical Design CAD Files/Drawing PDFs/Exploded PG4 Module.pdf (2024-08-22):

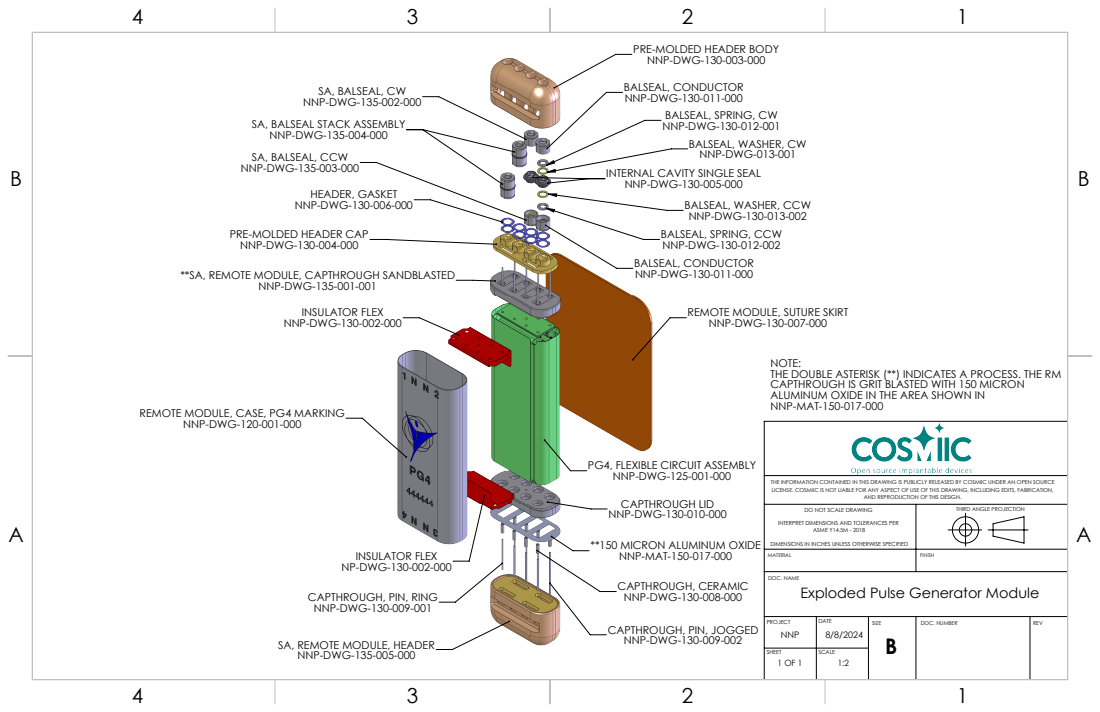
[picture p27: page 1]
HEADER, GASKET; INSULATOR FLEX; CAPTHROUGH, CERAMIC; DOC. NUMBER; REV; DOC. NAME; ASME Y14.5M - 2018

PRE-MOLDED HEADER BODY
NNP-DWG-130-003-000
BALSEAL, CONDUCTOR
NNP-DWG-130-011-000
BALSEAL, SPRING, CW
NNP-DWG-130-012-001
BALSEAL, WASHER, CW
NNP-DWG-013-001

SA, BALSEAL, CW
NNP-DWG-135-002-000

SA, BALSEAL STACK ASSEMBLY
NNP-DWG-135-004-000
SA, BALSEAL, CCW
NNP-DWG-135-003-000

INTERNAL CAVITY SINGLE SEAL
NNP-DWG-130-005-000

BALSEAL, WASHER, CCW
NNP-DWG-130-013-002
BALSEAL, SPRING, CCW
NNP-DWG-130-012-002

PRE-MOLDED HEADER CAP
NNP-DWG-130-004-000

**SA, REMOTE MODULE, CAPTHROUGH SANDBLASTED

REMOTE MODULE, SUTURE SKIRT
NNP-DWG-130-007-000

NOTE:
THE DOUBLE ASTERISK (**) INDICATES A PROCESS. THE RM
CAPTHROUGH IS GRIT BLASTED WITH 150 MICRON
ALUMINUM OXIDE IN THE AREA SHOWN IN
NNP-MAT-150-017-000

REMOTE MODULE, CASE, PG4 MARKING
NNP-DWG-120-001-000

PG4, FLEXIBLE CIRCUIT ASSEMBLY
NNP-DWG-125-001-000
CAPTHROUGH LID
NNP-DWG-130-010-000

THE INFORMATION CONTAINED IN THIS DRAWING IS PUBLICLY RELEASED BY COSMIIC UNDER AN OPEN SOURCE
LICENSE. COSMIIC IS NOT LIABLE FOR ANY ASPECT OF USE OF THIS DRAWING, INCLUDING EDITS, FABRICATION,

AND REPRODUCTION OF THIS DESIGN.

DO NOT SCALE DRAWING

THIRD ANGLE PROJECTION

INTERPRET DIMENSIONS AND TOLERANCES PER

**150 MICRON ALUMINUM OXIDE

DIMENSIONS IN INCHES UNLESS OTHERWISE SPECIFIED
Exploded Pulse Generator Module

CAPTHROUGH, PIN, RING
NNP-DWG-130-009-001

CAPTHROUGH, PIN, JOGGED
NNP-DWG-130-009-002

SA, REMOTE MODULE, HEADER
NNP-DWG-135-005-000

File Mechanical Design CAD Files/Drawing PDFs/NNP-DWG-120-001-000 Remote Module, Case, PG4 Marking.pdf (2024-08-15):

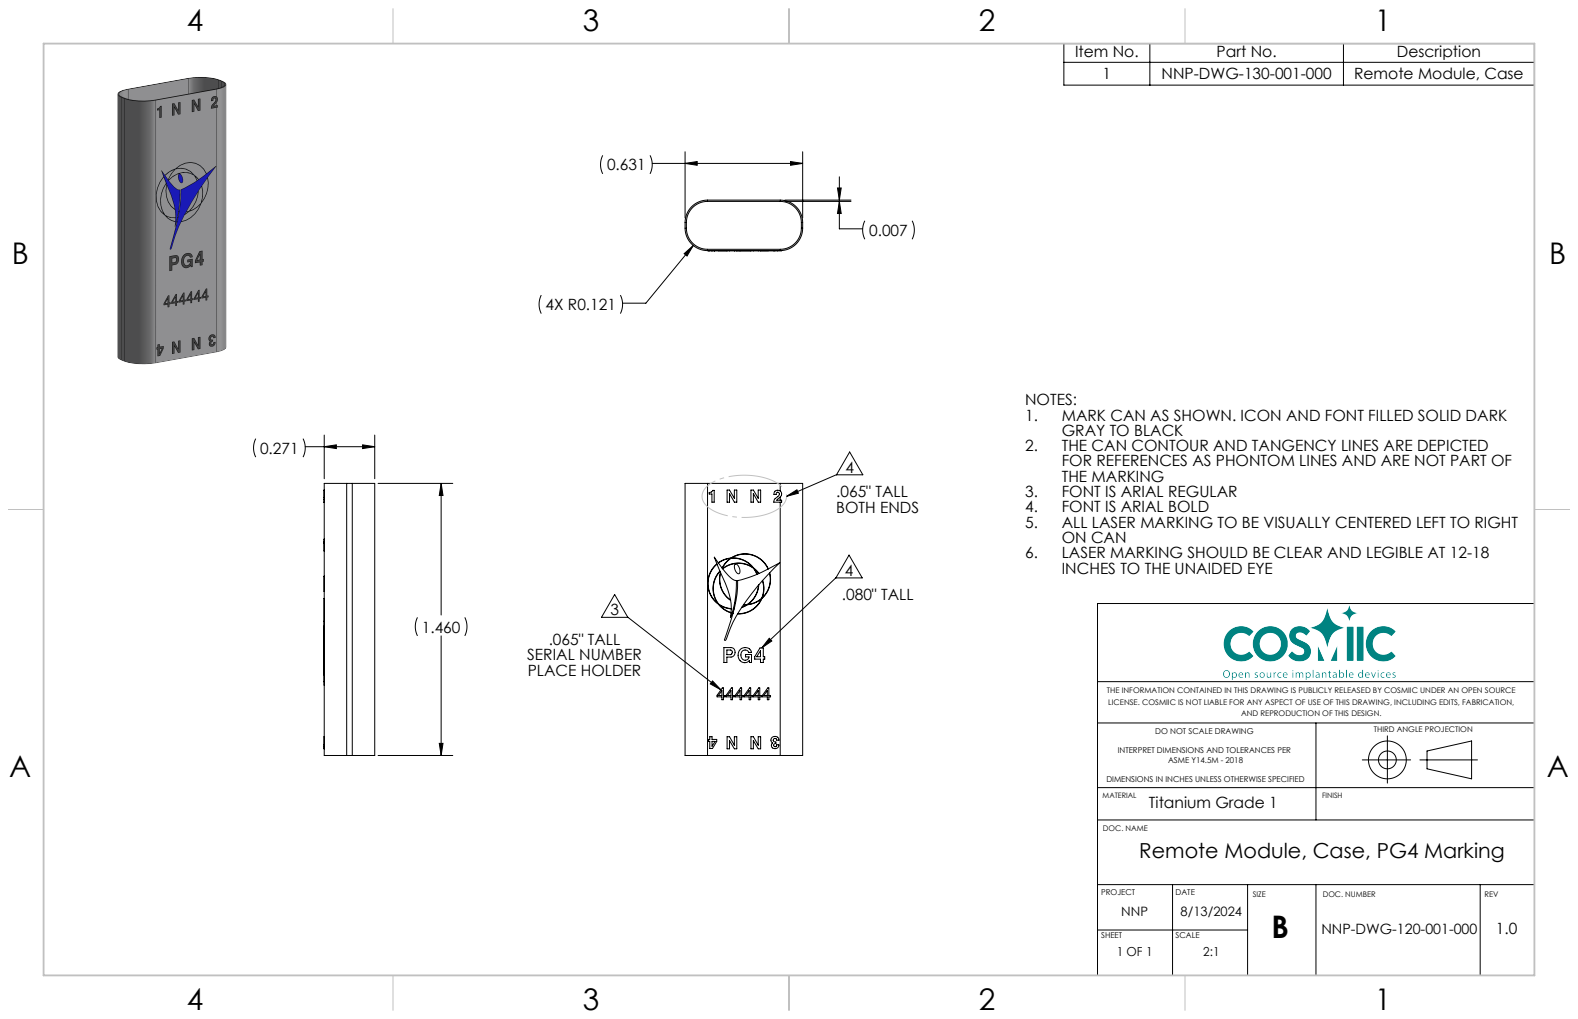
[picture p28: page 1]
.065" TALL BOTH ENDS; .080" TALL; .065" TALL SERIAL NUMBER PLACE HOLDER; DOC. NUMBER; REV; DOC. NAME

Item No. | Part No. | Description
1 | NNP-DWG-130-001-000 | Remote Module, Case

NOTES:
1. MARK CAN AS SHOWN. ICON AND FONT FILLED SOLID DARK
GRAY TO BLACK
2. THE CAN CONTOUR AND TANGENCY LINES ARE DEPICTED
FOR REFERENCES AS PHONTOM LINES AND ARE NOT PART OF
THE MARKING
3. FONT IS ARIAL REGULAR
4. FONT IS ARIAL BOLD
5. ALL LASER MARKING TO BE VISUALLY CENTERED LEFT TO RIGHT
ON CAN
6. LASER MARKING SHOULD BE CLEAR AND LEGIBLE AT 12-18
INCHES TO THE UNAIDED EYE

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

AND REPRODUCTION OF THIS DESIGN.

DO NOT SCALE DRAWING

THIRD ANGLE PROJECTION

INTERPRET DIMENSIONS AND TOLERANCES PER

ASME Y14.5M - 2018
Titanium Grade 1
Remote Module, Case, PG4 Marking
NNP-DWG-120-001-000

DIMENSIONS IN INCHES UNLESS OTHERWISE SPECIFIED

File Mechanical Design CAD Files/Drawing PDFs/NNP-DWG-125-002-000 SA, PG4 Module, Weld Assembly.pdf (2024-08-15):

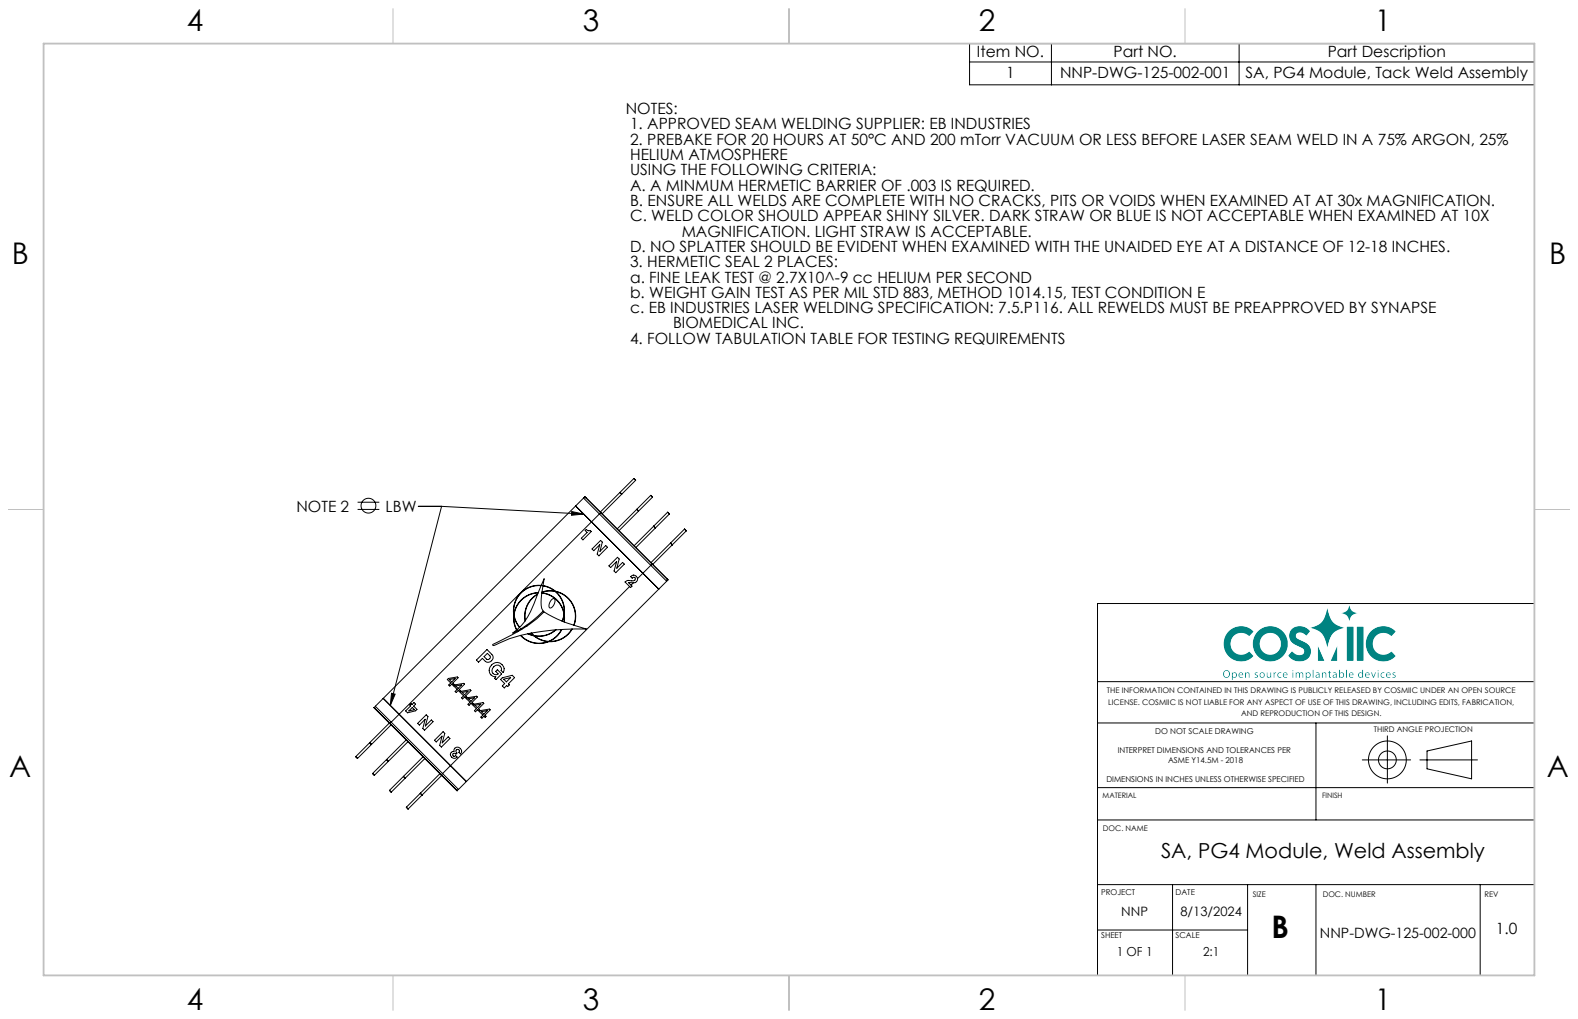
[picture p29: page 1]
NOTE 2; LBW; DOC. NUMBER; REV; DOC. NAME; ASME Y14.5M - 2018

Item NO. | Part NO. | Part Description
1 | NNP-DWG-125-002-001 | SA, PG4 Module, Tack Weld Assembly

NOTES:
1. APPROVED SEAM WELDING SUPPLIER: EB INDUSTRIES
2. PREBAKE FOR 20 HOURS AT 50°C AND 200 mTorr VACUUM OR LESS BEFORE LASER SEAM WELD IN A 75% ARGON, 25%
HELIUM ATMOSPHERE
USING THE FOLLOWING CRITERIA:
A. A MINMUM HERMETIC BARRIER OF .003 IS REQUIRED.
B. ENSURE ALL WELDS ARE COMPLETE WITH NO CRACKS, PITS OR VOIDS WHEN EXAMINED AT AT 30x MAGNIFICATION.
C. WELD COLOR SHOULD APPEAR SHINY SILVER. DARK STRAW OR BLUE IS NOT ACCEPTABLE WHEN EXAMINED AT 10X
MAGNIFICATION. LIGHT STRAW IS ACCEPTABLE.
D. NO SPLATTER SHOULD BE EVIDENT WHEN EXAMINED WITH THE UNAIDED EYE AT A DISTANCE OF 12-18 INCHES.
3. HERMETIC SEAL 2 PLACES:
a. FINE LEAK TEST @ 2.7X10^-9 cc HELIUM PER SECOND
b. WEIGHT GAIN TEST AS PER MIL STD 883, METHOD 1014.15, TEST CONDITION E
c. EB INDUSTRIES LASER WELDING SPECIFICATION: 7.5.P116. ALL REWELDS MUST BE PREAPPROVED BY SYNAPSE
BIOMEDICAL INC.
4. FOLLOW TABULATION TABLE FOR TESTING REQUIREMENTS

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

AND REPRODUCTION OF THIS DESIGN.

DO NOT SCALE DRAWING

THIRD ANGLE PROJECTION

INTERPRET DIMENSIONS AND TOLERANCES PER

DIMENSIONS IN INCHES UNLESS OTHERWISE SPECIFIED
SA, PG4 Module, Weld Assembly
NNP-DWG-125-002-000

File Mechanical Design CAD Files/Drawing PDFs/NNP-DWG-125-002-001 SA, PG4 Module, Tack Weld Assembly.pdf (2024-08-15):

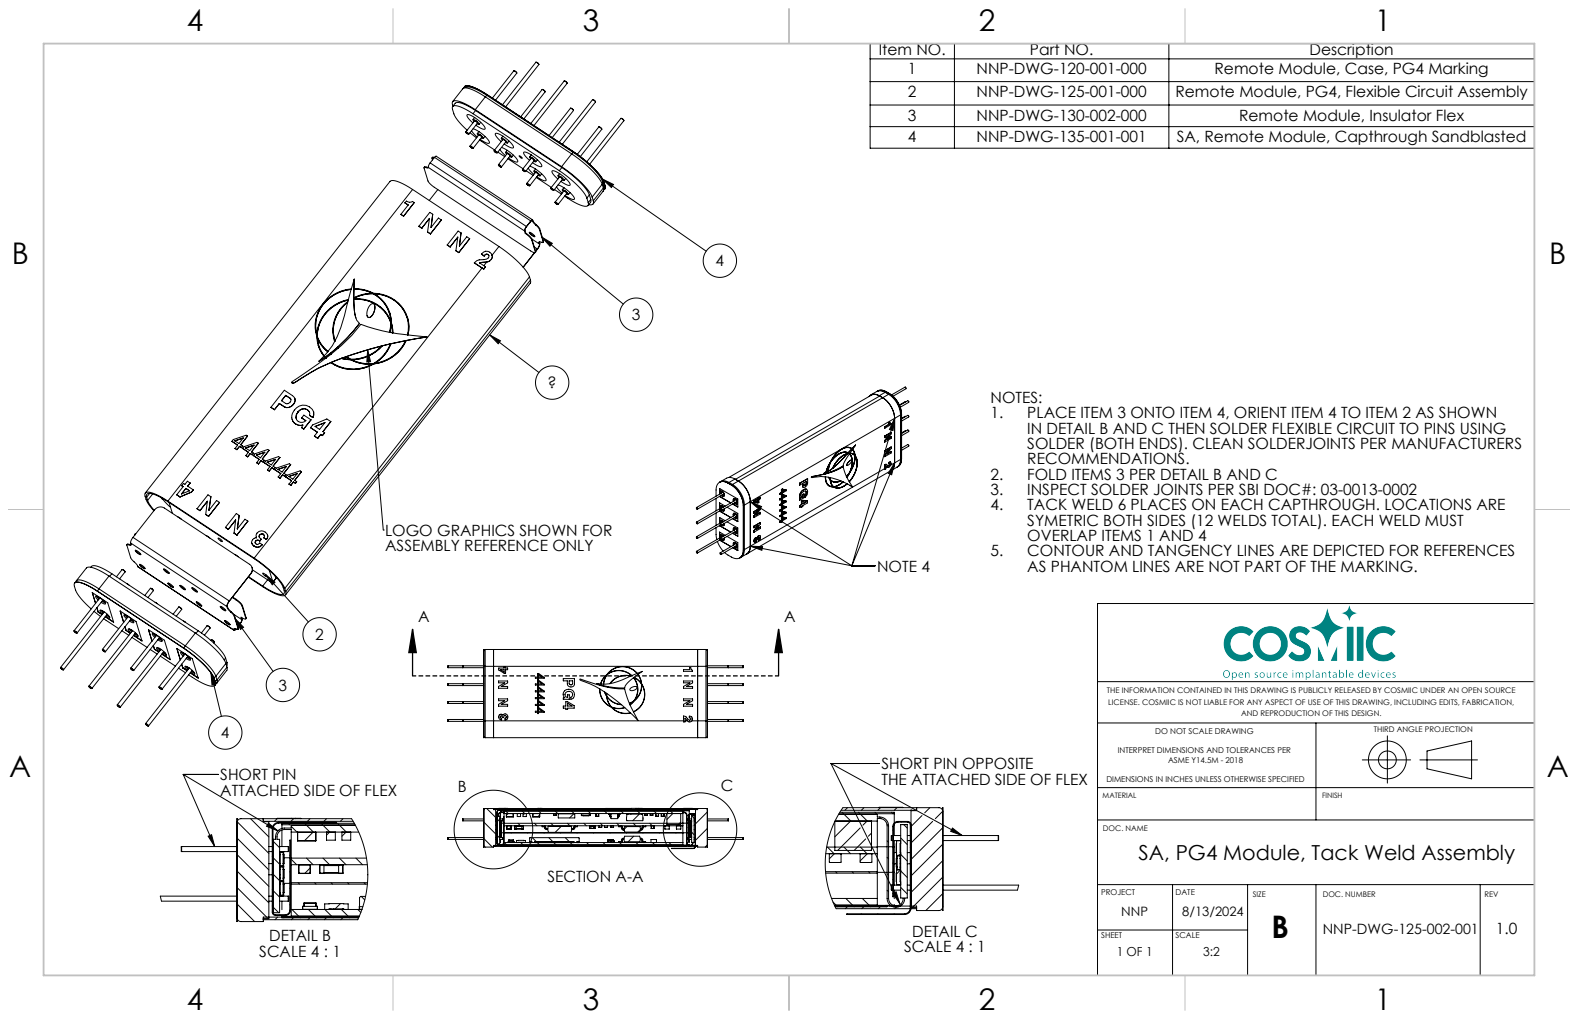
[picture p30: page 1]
NOTE 4; SECTION A-A; DETAIL B SCALE 4 : 1; DETAIL C SCALE 4 : 1; DOC. NUMBER; REV; DOC. NAME; ASME Y14.5M - 2018

Item NO. | Part NO. | Description
1 | NNP-DWG-120-001-000 | Remote Module, Case, PG4 Marking
2 | NNP-DWG-125-001-000 | Remote Module, PG4, Flexible Circuit Assembly
3 | NNP-DWG-130-002-000 | Remote Module, Insulator Flex
4 | NNP-DWG-135-001-001 | SA, Remote Module, Capthrough Sandblasted

NOTES:
1. PLACE ITEM 3 ONTO ITEM 4, ORIENT ITEM 4 TO ITEM 2 AS SHOWN
IN DETAIL B AND C THEN SOLDER FLEXIBLE CIRCUIT TO PINS USING
SOLDER (BOTH ENDS). CLEAN SOLDERJOINTS PER MANUFACTURERS
RECOMMENDATIONS.
2. FOLD ITEMS 3 PER DETAIL B AND C
3. INSPECT SOLDER JOINTS PER SBI DOC#: 03-0013-0002
4. TACK WELD 6 PLACES ON EACH CAPTHROUGH. LOCATIONS ARE
SYMETRIC BOTH SIDES (12 WELDS TOTAL). EACH WELD MUST
OVERLAP ITEMS 1 AND 4
5. CONTOUR AND TANGENCY LINES ARE DEPICTED FOR REFERENCES
AS PHANTOM LINES ARE NOT PART OF THE MARKING.

LOGO GRAPHICS SHOWN FOR
ASSEMBLY REFERENCE ONLY

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

AND REPRODUCTION OF THIS DESIGN.

DO NOT SCALE DRAWING

THIRD ANGLE PROJECTION

INTERPRET DIMENSIONS AND TOLERANCES PER

SHORT PIN OPPOSITE
THE ATTACHED SIDE OF FLEX

SHORT PIN
ATTACHED SIDE OF FLEX

DIMENSIONS IN INCHES UNLESS OTHERWISE SPECIFIED
SA, PG4 Module, Tack Weld Assembly
NNP-DWG-125-002-001

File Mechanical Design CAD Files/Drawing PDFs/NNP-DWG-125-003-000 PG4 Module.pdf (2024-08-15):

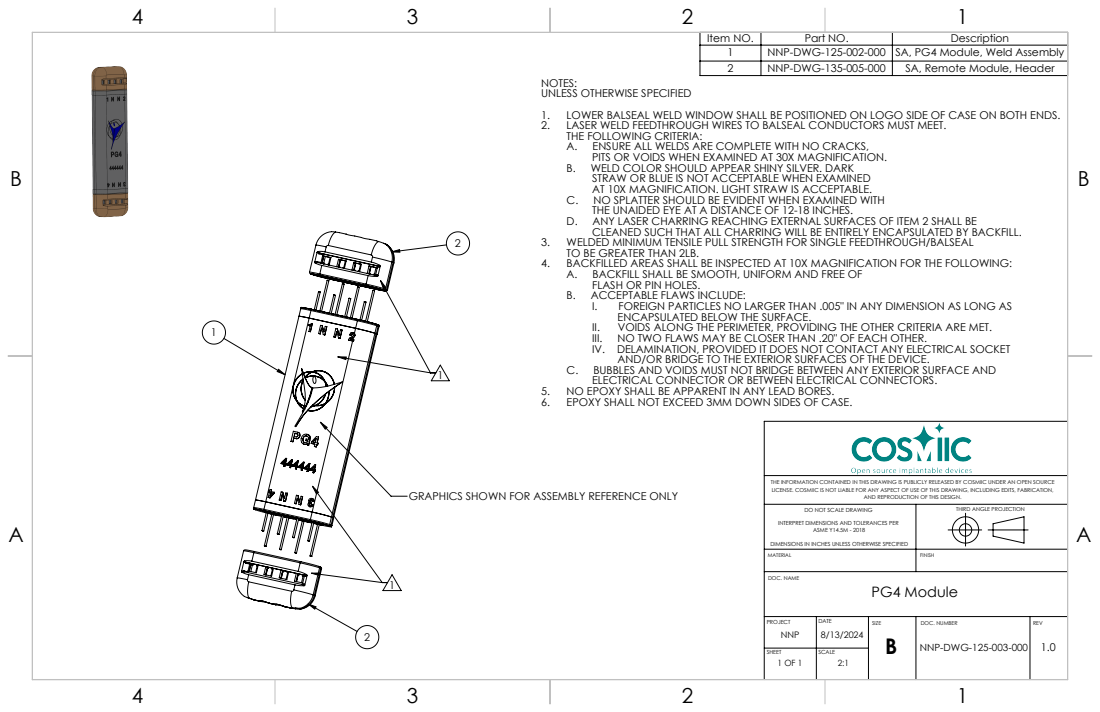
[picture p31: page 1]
VOIDS ALONG THE PERIMETER, PROVIDING THE OTHER CRITERIA ARE MET.; DOC. NUMBER; REV; DOC. NAME; ASME Y14.5M - 2018; NNP-DWG-125-003-000 1.0; PG4 Module

Item NO. | Part NO. | Description
1 | NNP-DWG-125-002-000 | SA, PG4 Module, Weld Assembly
2 | NNP-DWG-135-005-000 | SA, Remote Module, Header

NOTES:
UNLESS OTHERWISE SPECIFIED
1. LOWER BALSEAL WELD WINDOW SHALL BE POSITIONED ON LOGO SIDE OF CASE ON BOTH ENDS.
2. LASER WELD FEEDTHROUGH WIRES TO BALSEAL CONDUCTORS MUST MEET.
THE FOLLOWING CRITERIA:
A. ENSURE ALL WELDS ARE COMPLETE WITH NO CRACKS,
PITS OR VOIDS WHEN EXAMINED AT 30X MAGNIFICATION.
B. WELD COLOR SHOULD APPEAR SHINY SILVER. DARK
STRAW OR BLUE IS NOT ACCEPTABLE WHEN EXAMINED
AT 10X MAGNIFICATION. LIGHT STRAW IS ACCEPTABLE.
C. NO SPLATTER SHOULD BE EVIDENT WHEN EXAMINED WITH
THE UNAIDED EYE AT A DISTANCE OF 12-18 INCHES.
D. ANY LASER CHARRING REACHING EXTERNAL SURFACES OF ITEM 2 SHALL BE
CLEANED SUCH THAT ALL CHARRING WILL BE ENTIRELY ENCAPSULATED BY BACKFILL.
TO BE GREATER THAN 2LB.
4. BACKFILLED AREAS SHALL BE INSPECTED AT 10X MAGNIFICATION FOR THE FOLLOWING:
A. BACKFILL SHALL BE SMOOTH, UNIFORM AND FREE OF
FLASH OR PIN HOLES.
B. ACCEPTABLE FLAWS INCLUDE:
I. FOREIGN PARTICLES NO LARGER THAN .005" IN ANY DIMENSION AS LONG AS
ENCAPSULATED BELOW THE SURFACE.
III. NO TWO FLAWS MAY BE CLOSER THAN .20" OF EACH OTHER.
IV. DELAMINATION, PROVIDED IT DOES NOT CONTACT ANY ELECTRICAL SOCKET
AND/OR BRIDGE TO THE EXTERIOR SURFACES OF THE DEVICE.
ELECTRICAL CONNECTOR OR BETWEEN ELECTRICAL CONNECTORS.

3. WELDED MINIMUM TENSILE PULL STRENGTH FOR SINGLE FEEDTHROUGH/BALSEAL

C. BUBBLES AND VOIDS MUST NOT BRIDGE BETWEEN ANY EXTERIOR SURFACE AND
5. NO EPOXY SHALL BE APPARENT IN ANY LEAD BORES.
6. EPOXY SHALL NOT EXCEED 3MM DOWN SIDES OF CASE.

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

GRAPHICS SHOWN FOR ASSEMBLY REFERENCE ONLY

AND REPRODUCTION OF THIS DESIGN.

DO NOT SCALE DRAWING

THIRD ANGLE PROJECTION

INTERPRET DIMENSIONS AND TOLERANCES PER

DIMENSIONS IN INCHES UNLESS OTHERWISE SPECIFIED

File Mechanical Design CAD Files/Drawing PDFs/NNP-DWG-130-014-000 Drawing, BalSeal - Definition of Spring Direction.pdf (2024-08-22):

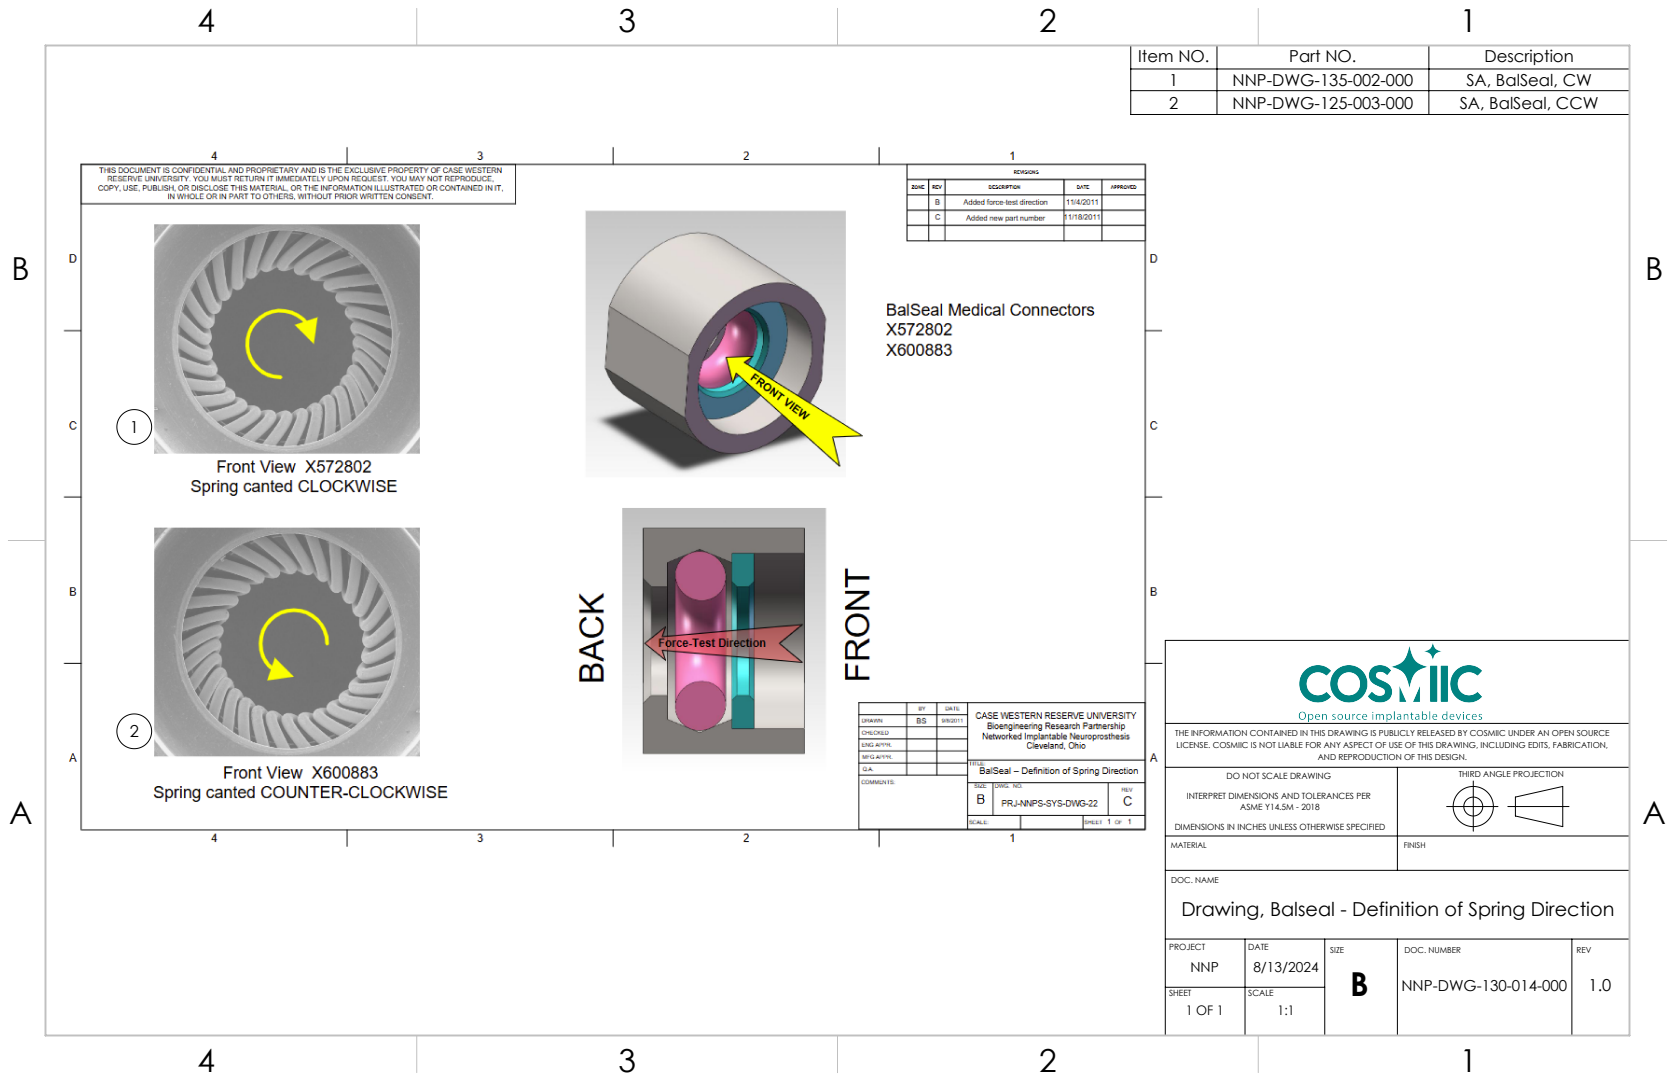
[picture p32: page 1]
DOC. NUMBER; REV; ASME Y14.5M - 2018

Item NO. | Part NO. | Description
1 | NNP-DWG-135-002-000 | SA, BalSeal, CW
2 | NNP-DWG-125-003-000 | SA, BalSeal, CCW

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

AND REPRODUCTION OF THIS DESIGN.

DO NOT SCALE DRAWING

THIRD ANGLE PROJECTION

INTERPRET DIMENSIONS AND TOLERANCES PER

DIMENSIONS IN INCHES UNLESS OTHERWISE SPECIFIED

DOC. NAME
Drawing, Balseal - Definition of Spring Direction

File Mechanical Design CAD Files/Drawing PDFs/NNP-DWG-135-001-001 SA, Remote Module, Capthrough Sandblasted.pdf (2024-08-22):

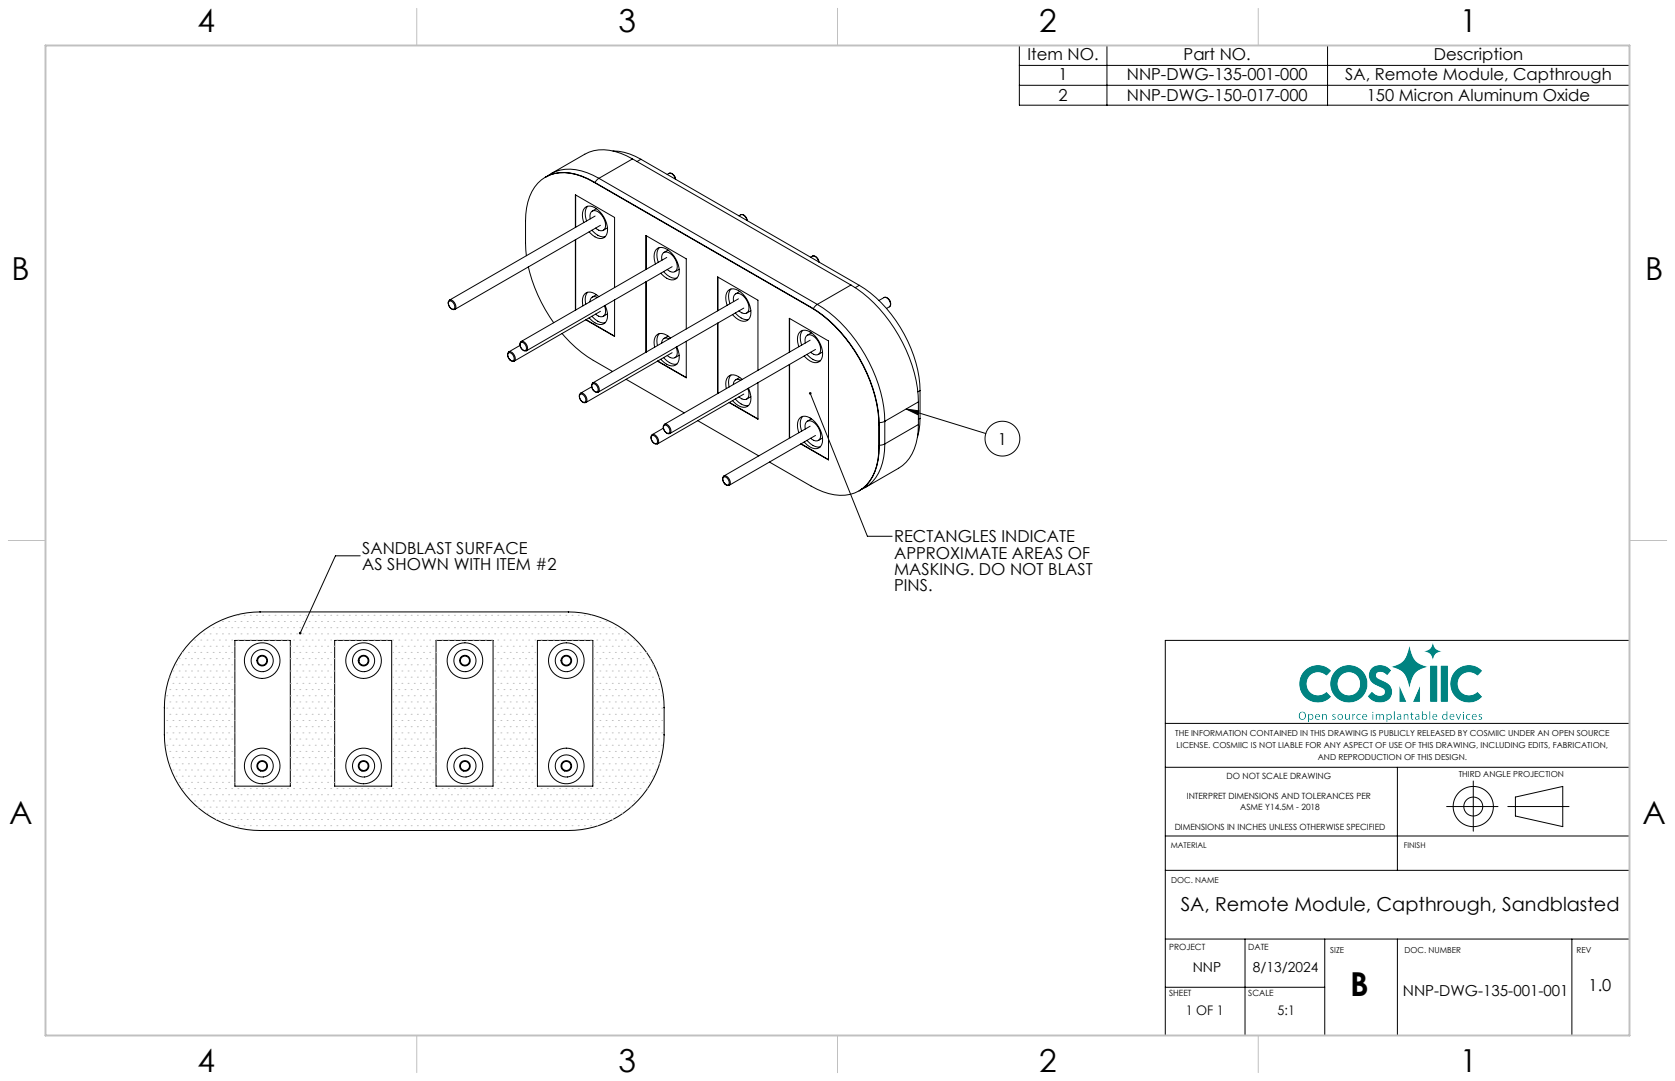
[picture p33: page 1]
DOC. NUMBER; REV; ASME Y14.5M - 2018

Item NO. | Part NO. | Description
1 | NNP-DWG-135-001-000 | SA, Remote Module, Capthrough
2 | NNP-DWG-150-017-000 | 150 Micron Aluminum Oxide

RECTANGLES INDICATE
APPROXIMATE AREAS OF
MASKING. DO NOT BLAST
PINS.

SANDBLAST SURFACE
AS SHOWN WITH ITEM #2

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

AND REPRODUCTION OF THIS DESIGN.

DO NOT SCALE DRAWING

THIRD ANGLE PROJECTION

INTERPRET DIMENSIONS AND TOLERANCES PER

DIMENSIONS IN INCHES UNLESS OTHERWISE SPECIFIED

DOC. NAME
SA, Remote Module, Capthrough, Sandblasted

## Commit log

2024-08-13 Uploading PG4 Files
    [NNP-DWG-130-001-000 Remote Module, Case, No Marking.SLDPRT, NNP-DWG-130-001-000 Remote Module, Case, No Marking.STEP, NNP-DWG-130-001-000 Remote Module, Case.S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]
2024-08-14 updating balseal drawings with latest revision
    [NNP-DWG-130-015-000 Drawing, BalSeal - Definition of Spring Dircetion.SLDDRW, NNP-DWG-130-015-000 Drawing, BalSeal - Definition of Spring Direction.SLDDRW, NNP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]
2024-08-15 Updated PG4 file part numbers to be unique to PG4
    [NNP-DWG-120-001-000 Remote Module, Case, PG4 Marking.SLDASM, NNP-DWG-120-001-000 Remote Module, Case, PG4 Marking.SLDDRW, NNP-DWG-120-001-000 Remote Module, Ca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]
2024-08-22 Updating part numbers based on changing 150 micron part number
    [NNP-DWG-120-001-000 Remote Module, Case, PG4 Marking.SLDASM, NNP-DWG-125-002-000 SA, PG4 Module, Weld Assembly.SLDASM, NNP-DWG-125-002-001 SA, PG4 Module, Tack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]
2025-03-11 Posting PG4 PCB design files
    [NNP-DWG-125-001-000 PG4 Schematic Drawing Pg1.SchDoc, NNP-DWG-125-001-000 PG4 Schematic Drawing Pg2.SchDoc, NNP-DWG-125-001-000 PG4 Schematic Drawing Pg3.SchDo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]
2025-08-28 Adding Altium design files
    [NNP-DWG-125-001-000 PG4 BOM.xlsx, PG4D.GBL, PG4D.GBP, PG4D.GBS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]
